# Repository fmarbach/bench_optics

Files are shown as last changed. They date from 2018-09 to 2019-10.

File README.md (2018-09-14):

## Basic Bench Optics
The repository contains the Mrsic-Flogel optics practical handout. 
This is based on the [TENSS](http://www.tenss.ro/) basic [bench optics exercises](https://github.com/tenss/bench_optics). 
You can find the latest PDF of the hand-out in the project's [Releases](https://github.com/BaselLaserMouse/bench_optics/releases).

Parts lists are supplied in `.txt` files separate from the `.tex` and `.pdf`.

### Contributing
The handout is written in Latex. 
Please do not push PDFs of the built handout to the repository because it bloats the repository.
Instead, you can upload PDFs to a release.

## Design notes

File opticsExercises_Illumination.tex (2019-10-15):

%%%%%%%%%%%%%%%%%%%%%%%%%%%%%%%%%%%%%%%%%%%%%%%%%%%%%%%%%%%%%%%%%%%%%%%
%%%%  Load the document class and packages                         %%%%
%%%%%%%%%%%%%%%%%%%%%%%%%%%%%%%%%%%%%%%%%%%%%%%%%%%%%%%%%%%%%%%%%%%%%%%
\documentclass[a4paper]{report}
\usepackage{epsfig}            % to insert PostScript figures
\graphicspath{ 
  {figures/} 
}

%Change figure names
\renewcommand{\figurename}{Fig}

\usepackage[bf,footnotesize]{caption} % make captions small and label bold

\addtocounter{chapter}{1} %Because starting at zero is silly
\makeatletter
\renewcommand{\thesection}{\@arabic\c@section}
\renewcommand{\thefigure}{\@arabic\c@figure}
\makeatother

\usepackage[a4paper,margin=2.7cm,tmargin=2.5cm,bmargin=2.5cm]{geometry} 
\usepackage{textcomp}          % To make nice degree symbols and others\usepackage[bf,footnotesize]{caption} % make captions small and label bold
\usepackage{wrapfig}
%to produce the clickable references along the left in Acroread. This
%package must be included last. 
\usepackage[ps2pdf,bookmarks=TRUE]{hyperref} 

\usepackage{wasysym}

%%%%%%%%%%%%%%%%%%%%%%%%%%%%%%%%%%%%%%%%%%%%%%%%%%%%%%%%%%%%%%%%%%%%%%%
%%%%  Hypertext references for Acrobat                             %%%%
%%%%%%%%%%%%%%%%%%%%%%%%%%%%%%%%%%%%%%%%%%%%%%%%%%%%%%%%%%%%%%%%%%%%%%%
\hypersetup{
pdfauthor = {SWC},
pdftitle = {Optics Exercises},
pdfkeywords = {optics, lenses, refraction, reflection, dispersion,
  telescope, microscope},
pdfcreator = {LaTeX with hyperref},
pdfproducer = {dvips + ps2pdf}
           }

\begin{document}

%set the number of sectioning levels 
\setcounter{secnumdepth}{2}

\begin{center}
\textbf{\Large{Optics Bench Exercises \\ \vspace{5mm} Building a brightfield microscope}}
\end{center}

\vspace{10mm}

The goal of this exercise is to build a brightfield microscope with K\"{o}hler illumination. We will do this in steps to understand the importance of illuminating the sample uniformly and from a wide range of angles. Important: think about WHY we make you place specific parts in a specific order.

\section{Critical illumination of a sample}
In critical illumination the light source is focused onto the specimen.
This provides illumination from a range of angles but has a major drawback which will become apparent soon. 

\subsection{Optical axis}
We will first create an 'optical axis' using a laser pointer - this will help us align the optics. Set the laser at one end of the rail and align the beam with the rail (horizontal and centred) using a single iris:
\begin{itemize}
    \setlength\itemsep{0.1em}
    \item Set the iris to a height suitable for adding 2'' optics. You can mount the iris to a $75~mm$ post and use a $50~mm$ post holder. 
    \item Clamp the laser pointer to one end of the rail.
    \item With the iris closest to the pointer, \textit{move/translate} the pointer until it goes through the iris. 
    \item Slide the iris to the other end of the rail and \textit{tilt} the pointer until it goes through the iris. 
    \item Repeat until the beam is parallel with the rail. 
\end{itemize} 

\begin{figure}[h]
\center

\caption{Aligning a laser beam to the rail using an iris.}
\label{fig:beam_iris}
\end{figure}

\clearpage

\subsection{Imaging optics}
Once you're done, place a positioning collar around the iris post so you can retain its height even if you have to remove it from the post holder. We start at the end of the microscope, with the tube lens and objective (Fig.~\ref{fig:beam_obj_tube}). 

\begin{itemize}
\item Hint: In addition to the iris, use `back reflections' of the laser to align optics
\item Slide the iris to the end of the rail. 
\item Place the $f=300~mm$ lens $1f$ from the iris and adjust it until the beam goes through the iris. This is your `tube lens'.
\item Place the 4x objective before the tube lens and align it such that the beam (now expanded) again goes through the iris. What is the magnification of your imaging system?
\item Why are we starting from the back of the microscope? Why the tube lens first?
\end{itemize}

\begin{figure}[h]
\center

\caption{Aligning the tube lens and objective with the beam.}
\label{fig:beam_obj_tube}
\end{figure}

\subsection{Basic illumination optics}
Let's place a sample and illuminate it with an LED, completing our simple microscope.

\begin{itemize}
\item Hint: Use $30~mm$ or $40~mm$ posts for the 2'' lenses, sample holder, and card holder.
\item Place your sample holder in front of the objective (about mid-rail)
\item Place the LED and choose one of the 1''{\diameter} $f=25~mm$ or $f=35~mm$ lenses to direct light onto the sample. Can you see the image of the LED? Where does the image form?
\item At the other end of the rail where the iris was, place a viewing screen onto which you will form an image - move the objective to focus.
\end{itemize}

The above arrangement is a simple microscope. How can you modify the illumination to make it brighter? Discuss with a TA and Implement it.
\\

You now have an infinite conjugate illumination system, giving you control over the illumination NA by placing an iris in the infinite space. Draw the ray diagram to predict what effect this has on the image. Test it with a sample! (Fig.~\ref{fig:critical_iris}).
\\

\subsection{Upgrade to K\"{o}hler illumination}
Discuss what is missing/wrong with your microscope. 

\begin{itemize}
	\item Use your K\"{o}hler notes to reason through this and implement the necessary changes
	\item Find ways to verify that your microscope is well aligned (optics placed in correct positions). Do you have independent control over illumination field and NA?
	\item Add the camera, check out different samples
	\item Impress a TA with your accomplishment
	\item Switch to a 10x objective - what determines how well you can image the sample? What is better compared to the 4x?
\end{itemize}

\begin{figure}[h]
\center


\caption{Critical illumination with two lenses. 
There is an iris after that collector lens that is open on the left image and closed on the right image. 
Note how closing the iris restricts the range of angles reaching the sample.}
\label{fig:critical_iris}
\end{figure}

\vspace{30mm}
You have finished! Unfortunately, the princess is another castle. See you tomorrow.

\clearpage

\section{Reference: K\"{o}hler Illumination}
K\"{o}hler illumination is an important and commonly used technique in light microscopy, as it provides even illumination of the sample whilst ensuring the light source (e.g. the bulb filament) is not visible. 
This is achieved by adding a third lens, the field lens, before the condenser so that the image of the light source is out of focus at the sample. 
Since the source is out of focus, the illumination is uniform. 
Instead, the image is formed at $1f$ from the field lens. 
The condenser is then located at $1f$ from this image (as in a beam expander) so collimated (i.e. out of focus) light reaches the sample. 

The key to understanding K\"{o}hler illumination is to consider the two sets of conjugate planes in the system (Fig.~\ref{fig:koehler}). 
The \textbf{sample} is, of course, conjugate with the image plane but it also conjugate with a point $1f$ from the collector lens ($f_{CL}$ in Fig.~\ref{fig:koehler}). 
The \textbf{light source} is conjugate with a location between the field lens and the condenser ($f_F$ and $f_{CO}$ in Fig.~\ref{fig:koehler}). 
The light source is also conjugate with the objective back aperture (not shown in Fig.~\ref{fig:koehler}). 

\begin{figure}[ht]
\center

\caption{K\"{o}hler Illumination. 
The blue lines indicate the conjugate relationship between the sample plane and the location of the field diaphragm.
The yellow lines indicate the conjugate relationship between the light source plane and the location of the aperture diaphragm.
}
\label{fig:koehler}
\end{figure}

At the two conjugate planes in the illumination path are two irises (diaphragms). 
The \textbf{field diaphragm} is at $1f$ before the field lens, in the point conjugate with the sample. 
The field lens and condenser lens form an infinite conjugate system that image the field diaphragm onto the sample. 
The field diaphragm appears in focus at the sample and is used to regulate the area of illumination. 
This helps to improve contrast by minimizing stray light. 
Remember, the The \textbf{f}ield planes are the image \textbf{f}orming planes. 

The \textbf{aperture diaphragm} is located in the plane conjugate with the light source. 
i.e. it is located where an image of the light source is formed. 
Opening and closing this diaphragm regulates which regions of the light source can contribute to the illumination. 
Closing the diaphragm blocks off-axis regions of the light source and stops them from generating the more oblique rays that come out of the condenser. 
Closing the aperture diaphragm reduces the NA of the illumination and increases depth of field. 

\clearpage

The completed arrangement of the components is shown in Fig.~\ref{fig:koehler_completed}. 
The components will be arranged in the following order and are all at $1f$ from each other (Fig.~\ref{fig:koehler}):
\begin{enumerate}
\setlength\itemsep{0.1em}
\item Collector lens
\item Field diaphragm.
\item Field lens ($f=60$)
\item Aperture diaphragm
\item Condenser lens ($f=60$)
\item The objective and tube lenses as before.
\end{enumerate}

\begin{figure}[h]
\center

\caption{The completed K\"{o}hler illumination assembly on a rail.}
\label{fig:koehler_completed}
\end{figure}

\end{document}

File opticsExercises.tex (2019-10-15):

%%%%%%%%%%%%%%%%%%%%%%%%%%%%%%%%%%%%%%%%%%%%%%%%%%%%%%%%%%%%%%%%%%%%%%%
%%%%  Load the document class and packages                         %%%%
%%%%%%%%%%%%%%%%%%%%%%%%%%%%%%%%%%%%%%%%%%%%%%%%%%%%%%%%%%%%%%%%%%%%%%%
\documentclass[a4paper]{report}
\usepackage{epsfig}            % to insert PostScript figures
\graphicspath{ 
	{./figures/} 
}

%Change figure names
\renewcommand{\figurename}{Fig}

\usepackage[bf,footnotesize]{caption} % make captions small and label bold

\addtocounter{chapter}{1} %Because starting at zero is silly
\makeatletter
\renewcommand{\thesection}{\@arabic\c@section}
\renewcommand{\thefigure}{\@arabic\c@figure}
\makeatother

\usepackage[a4paper,margin=2.7cm,tmargin=2.5cm,bmargin=2.5cm]{geometry} 
\usepackage{textcomp}          % To make nice degree symbols and others\usepackage[bf,footnotesize]{caption} % make captions small and label bold
\usepackage{wrapfig}
%to produce the clickable references along the left in Acroread. This
%package must be included last. 
\usepackage[ps2pdf,bookmarks=TRUE]{hyperref} 

%%%%%%%%%%%%%%%%%%%%%%%%%%%%%%%%%%%%%%%%%%%%%%%%%%%%%%%%%%%%%%%%%%%%%%%
%%%%  Hypertext references for Acrobat                             %%%%
%%%%%%%%%%%%%%%%%%%%%%%%%%%%%%%%%%%%%%%%%%%%%%%%%%%%%%%%%%%%%%%%%%%%%%%
\hypersetup{
	pdfauthor = {SWC},
	pdftitle = {Optics Exercises},
	pdfkeywords = {optics, lenses, refraction, reflection, dispersion,
		telescope, microscope},
	pdfcreator = {LaTeX with hyperref},
	pdfproducer = {dvips + ps2pdf}
}

\begin{document}

	%set the number of sectioning levels 
	\setcounter{secnumdepth}{2}
	
	\begin{center}
		\textbf{\Large{Optics Bench Exercises: Image Formation}}
	\end{center}
	
	\section{Introduction}
	The goal of these exercises is to nurture an understanding of image formation, conjugate planes, and how multiple lenses interact in simple optical setups.

	\section{Before beginning}
	\begin{itemize}
		\item \textbf{Do not} force parts together. All parts should screw together or fit together easily.
		\item \textbf{Do not} over-tighten screws. Gentle pressure with a long-handled Allen key is sufficient. 
		\item \textbf{Do not} touch the coated surface of mirrors or optical filters. 
		\item Each group is responsible for tidying and organising their optical set at the end of the week. All parts should be present and in their correct locations as shown on the course wiki page. 
		
	\end{itemize}
	
	\section{Equipment usage notes}
	The black post holders mount to the rail carriages via a short cap screw as shown in Fig.~\ref{fig:post}. 
	The carriages can then be attached to the rail, on which they can slide up and down. 
	Use the lens tool to secure lenses in lens holders. 
	`SM2' refers to two inch optics and associated accessories. 
	`SM1' refers to one inch optics and associated accessories. 
	
	\begin{figure}[h]
		\center
		
		
		
		\caption{A post holder bolted to a rail carriage (left \& middle).
			The lens tools secure lenses in the holders using the rings (right).}
		\label{fig:post}
	\end{figure}

	\clearpage
	
	\section{Image Formation}
	An image is formed when all light rays leaving one point (or region) of the object arrive at some other defined point (or region) \textit{regardless of the angle of the ray}. 
	This is illustrated in Fig.~\ref{fig:imageforming}, where the brain cell on the left is imaged through an idealised thin lens (blue) to form the minified inverted image on the right. 
	All light rays leaving the brain cell's dendrite converge onto the inverted dendrite. 
	Each point in the image plane is illuminated by rays coming from a corresponding point in the object. 

	\begin{figure}[h]
		\center
		
		\caption{Simple image formation using one idealised thin lens (blue). 
			The focal length of the thin lens is $f$, object distance is $s_o$ and image distance is $s_i$. 
			The upper ray (parallel to the optical axis on the left) passes through the focal point (denoted as a dot) on the right side of the lens, the middle ray (passing through the centre of the lens) is unrefracted, and the lower ray passes through the focal point on the left side of the lens, and comes out parallel to the optical axis on the other side. 
		}
		\label{fig:imageforming}
	\end{figure}
	
	As the distance between the object and lens ($s_o$) is varied, the distance between the lens and image ($s_i$) also changes. This relationship is determined by the lens focal length ($f$) using the thin lens equation.
	
	\begin{equation}
	\frac{1}{s_o} + \frac{1}{s_i} = \frac{1}{f}
	\label{eq:thinlens}
	\end{equation}
	
	Sign conventions follow cartesion coordinates: $f>0$ for convex lenses, $f<0$ for concave lenses, $s_o$ is always $>0$, $s_i>0$ for real images, and $s_i<0$ for virtual images.
	Transverse distances above the optical axis are $>0$. Distances below are negative. 
	
	\vspace{2.5em}
	You will need to get comfortable with drawing ray diagrams, since you will do this later to explain what you observe on the bench.
	Copy the diagram in Fig.~\ref{fig:imageforming}.
	Draw the three cardinal rays:
	\begin{itemize}
		\item The ray parallel to the optical axis goes through $f$ on the image side.
		\item The ray that passes through the centre of the lens travels undeflected.
		\item Finally, the ray that goes through $f$ on the object side leaves the lens parallel to the optical axis on the image side. 
	\end{itemize}

	\clearpage

	\subsubsection{1. Determine the focal length of a convex lens }
	For the next few exercises you will use an LED as both a light source and an object to image.
	You will form various images of the LED emitter. 
	Your first task is to set up the LED on the optical rail:
	
	\begin{itemize}
		\item Attach a post holder to a rail carriage (Fig.~\ref{fig:post}) and place this on the rail. 
		\item Attach a 50~mm post to the white LED glued to a cage plate and place this in the post holder. 
		\item Power the LED using the ThorLabs LED driver. You will need the LED power cable.
	\end{itemize}

	Now choose a lens with a focal length of about $f=100~mm$ and attach the lens to a lens holder using the lens wrench and a retaining ring (this should already be in the lens holder).
	Mount the lens on another carriage and attach to the rail next to the LED. 
	Get the LED aligned with the middle of the lens (precise alignment isn't important). 
	
	You will use this lens to form an image of the LED.
	This is called \textbf{finite conjugate} imaging because the image is paired (i.e. conjugated) with an object at a finite distance from it.
	The image and sample planes are said to be \textbf{conjugate planes}.
	You will be able to form an image on a piece of card or paper if the distance between the lens and LED ($s_o$) is $>1f$.
	The image will be of the LED emitter, which  usually looks like a small bright square, often with fine lines going across it. 
	If all you see is a blur, you have not formed an image.
	
	\begin{itemize}
		\item Place the lens $<1f$ from the LED and use a piece of card on the other side of the lens to verify that no image is formed at any distance from the lens.
		\item Why is no image formed? 
		Hint: draw a diagram with the object at $<1f$. Plot just two rays: the undeflected ray and the ray coming out parallel with the optical axis and then going through $1f$ on the image side. 
		How do the rays behave after they have passed through the lens?
		
		\item Verify that an image is formed when the lens is $>1f$ from the LED: place a card very far from the LED (e.g. at $10f$ or $20f$) and slowly move the lens away from the LED. 
		What is the distance between the LED and the lens at which you see an image? 
		It should be just over $1f$.
		
		\item You could use the above approach to estimate the focal length of an unknown lens, however it's hard to tell when the source is at $1f$. 
		What is an easier way of estimating focal length? (Hint: you may not need the rail)
		
		\item What is the value of $s_i$ when $s_o=2f$?
	\end{itemize}

	\clearpage
	
	\subsubsection{2. Magnifying the image}
	As you might recall, the size of the image of the LED emitter varied with $s_o$.
	A lens produces images of different magnifications depending on $s_o$; an image can always be formed when $s_o>f$. 
	The magnification of a lens is calculated as follows:
	
	\begin{equation}
	M = \frac{h_i}{h_o} = \frac{s_i}{s_o} = \frac{f}{s_o-f}
	\label{eq:mag}
	\end{equation}
	
	A value of $M=1$ would mean unitary magnification (the image is the same size as the object). 
	Negative numbers indicate an inverted image.
	
	To begin thinking about magnification, hand-draw the ray diagram (as in Fig.~\ref{fig:imageforming}) for the smallest and largest values of $s_o$ that you used above. 
	Make sure to give yourself plenty of room. 
	Hint: You will run out of paper if you use values too close $1f$.
	If you're stuck, choose $1.5f$ and $4f$.
	Note the changing angles of the rays and how they lead to different image sizes as $s_o$ changes. 
	We will now see what happens when the rays come from infinity:
	
	\begin{itemize}
		\item Mount a lens of about $f=60~mm$ in a holder and attach a post to it. 
		Use it to form an image of the room lights on a piece of paper.
		The image is formed at $1f$.
		\item Repeat with a lens of about $f=100~mm$ lens. 
		What two things do you notice about the image? 
		\item Fig.~\ref{fig:outside} models the situation you saw. Satisfy yourself that this provides a reasonable explanation. 
		\item Go back to the lens and LED.
		Calculate the values of $s_o$ and $s_i$ which produce $M=-4$ (remember, negative just means inverted) for a $f=100~mm$ lens. 
		Measure the size of the LED image and so calculate the size of the LED emitter. 
		\item Remember the value of $s_i$ when $s_o=2f$? Therefore what is $M$ when $s_o=2f$?
	\end{itemize}

	\begin{figure}[h]
		\center
		
		\caption{Images formed at $1f$ from light originating at infinity. 
			The top is a $f=150~mm$ lens and the bottom a $f=50~mm$ lens.
			Light from different regions of the object arrive in parallel rays that come in at different angles (green and blue). 
			Each set of parallel rays come into focus at a point, satisfying the image-forming condition. }
		\label{fig:outside}
	\end{figure}

	What you have covered above demonstrates an important property of lenses: that they work the same both forwards and backwards.
	Recall the definition of an image-forming condition: \textbf{light rays leaving one point (or region) of the object arrive at some other defined point (or region)}.
	This is why no image was formed when the LED was at $s_o=f$, since rays leaving the lens are parallel and do not converge on the other side. 
	However, you \textit{were} able to form an image at $s_i=f$ when the object was very far away. 
	The ray diagrams of these two conditions are \textit{identical}--the only difference is that the object is at $1f$ in the first case and at infinity in the second case.
	
	\clearpage

	\subsubsection{3. Virtual images}
	At distances $s_o<f$, you were unable to form an image of the sample on the card because the rays emerging from the other side \textit{diverged}.
	\begin{itemize}
		\item Place the LED at $0.5f$ from a lens of your choice, observe the light diverging as it exits the lens.
		\item Draw the ray diagram for this $0.5f$ scenario:
		Draw the ray that leaves the tip of the object and continues undeflected through the middle of the lens. 
		Draw the ray that travels parallel to the optical axis and goes through $1f$ on the other side.
		See how these rays diverge. 
	\end{itemize}
	
	It would seem that no image is formed yet, surprisingly, a \textit{virtual image} is formed on the same side of the lens as the object. 
	This may sound like a peculiar concept, but you are already familiar with virtual images as this is how you see images in flat mirrors (Fig.~\ref{fig:mirror}). 
	The extended rays in the case of the mirror can be created from the \textit{diverging} rays from the object. 
	In the case of the the lens at $s_o<f$ we also have diverging rays and so can also draw extended rays as we did for the mirror. 
	Add the extended rays to your ray diagram by continuing the rays on the object side of the lens until they converge. 
	A virtual image is formed where they converge.
	What does your diagram tell you about the magnification of the virtual image?
	Verify this: pick up the lens, place it $<1f$ from an object and look through it.
	\begin{figure}[h]
		\center
		
		\caption{A virtual image of the bottle is created on the far side of the mirror. 
			This is described by the dotted lines which are `extended rays' that are used to form the virtual image. }
		\label{fig:mirror}
	\end{figure}
	
	A virtual image is also formed by a negative (concanve) lens, as shown in Fig.~\ref{fig:neglens}. 
	Examine the ray diagram of the negative lens. 
	What do you predict you will see if you look through a negative lens?
	Verify this with the $f=-50~mm$ lens.
	\begin{figure}[h]
		\center
		
		\caption{Ray diagram of a negative lens.}
		\label{fig:neglens}
	\end{figure}
	
	In summary, a \textbf{real image} is formed on the opposite side of the lens to the sample. 
	This allows the detector to be physically separated from the sample, which is rather useful.
	A \textbf{virtual image} is formed on the \textit{same} side of the lens as the object. 
	
	\clearpage
	
	\subsection{Infinite Conjugate}
	The \textbf{infinite conjugate} refers to the situation where the object is located at a distance of $1f$ from a lens (Fig.~\ref{infiniteConjugate}). 
	In this scenario the rays leaving the lens are parallel and do not converge, so this is not an image forming condition. 
	Instead, the image can be considered to be infinitely far away (hence the name). 
	If a second lens is added, then an image can be formed. 
	The magnification of the image is defined as Eq.~\ref{eq:magIC}. 
	This arrangement is useful because the image is always formed at $1f$ from the second lens irrespective of the distance between the lenses.
	Most microscope objectives are designed to work in this configuration since it allows filters to be added into the infinite space without altering the location of the image plane. 
	Such objectives are known as `infinity corrected', since they are designed to produce their best images with the sample at $1f$.
	
	\begin{equation}
	M=-\frac{f_2}{f_1}
	\label{eq:magIC}
	\end{equation}
	
	\begin{figure}[h]
		\center
		
		\caption{Two views of an infinite conjugate system made up of two $f=100~mm$ lenses. 
			The upper image shows on-axis rays only. 
			Note the rays are parallel in the infinite space.
			The lower diagram shows two additional sets of rays which arise from different off-axis locations and converge into corresponding locations in the image plane. }
		\label{infiniteConjugate}
	\end{figure}
	
	\begin{itemize}
		\item Set up two lenses with different focal lengths on the rail to build the infinite conjugate. 
		Ensure that the first lens is at $1f$ from the LED before placing the second lens. 
		\item Place a screen at the $f$ of the second and hold it in place with the post-mounted clip.
		\item Verify the consequences of the infinite space by moving the second lens and maintaining the screen at $f$ of the second lens. 
		What happens to the image size?
		\item Swap the first lens with one of a different focal length. 
		Verify that the image size changes in the manner in which you expect. 
	\end{itemize}

	\clearpage

	\subsection{Beam expanders}
	Lenses can be used to expand the diameter of a light beam, such a laser.
	Expanders can be built using either two convex lenses (Fig.~\ref{beamExpander1}) or a convex and concave lens (Fig.~\ref{beamExpander2}). 
	In both cases the lenses are set up such that their focal points coincide (i.e. they are separated by the sum of their focal lengths). 
	The image formed by the first lens is imaged at infinity by the second lens.
	The degree to which a beam is expanded is given by:
	\begin{equation}
	\frac{d_2}{d_1}=\frac{f_2}{f_1}
	\label{eq:beamExp}
	\end{equation}
	
	\begin{figure}[h]
		\center
		
		\caption{Beam expander with two convex lenses.}
		\label{beamExpander1}
	\end{figure}
	
	\begin{figure}[h]
		\center
		
		\caption{Beam expander with one convex and one concave lens.}
		\label{beamExpander2}
	\end{figure}
	
	We need collimated light (parallel rays) entering the system, so swap the LED for a laser pointer.
	You will align your laser to the rail (i.e. have the beam traveling parallel with the rail). 
	The lenses will then be aligned with respect to the beam. 
	This is an easy way of producing a well-aligned optical system and you will use the technique again and again throughout the course.
	The procedure is as follows:
	
	\begin{itemize}
		\item The laser is mounted in a 1'' tip/tilt mount. Screw this into a 1'' cage plate and attach this to one end of the rail via a 75 mm post (Fig.~\ref{fig:mounted_laser}).
		\item Power on the laser using the attached USB cable.
		\item Place the iris in a post next to the laser pointer, close it and adjust the height of the laser pointer and iris so the beam goes through the hole. 
		\item Slide the iris to the other end of the rail. 
		\item \textit{Rotate} the post the laser pointer sits on so it points at the iris aperture. Use the tip/tilt adjuster screws for fine adjustment.
		\textbf{Do not translate the laser pointer up and down.}
		\item Slide the pointer back down the rail and confirm that the beam still passes through hole. 
		If not, \textit{translate} the laser pointer's post up and down, then repeat the previous step.
	\end{itemize}
	
	\begin{figure}[h]
		\center
		%%\includegraphics[width=3in]{mounted_laser.eps}
		\caption{Laser mounted on a post.}
		\label{fig:mounted_laser}
	\end{figure}

	Now you will build a 3x beam expander $f=300~mm$ lens and an $f=100~mm$ lens. 
	These will be placed at the sum of their focal lengths and the laser pointer will be used as a guide for placing the lenses. 
	
	\begin{itemize}
		\item Place two more rail carriages onto the rail, between the iris and the laser pointer. 
		\item Place the $f=100~mm$ lens onto the post carriage nearest the laser and position the iris roughly $1f$ from the lens.
		\item You will know the lens is at the correct height because the beam will hit the middle of the iris. 
		If you look carefully at the lens surface, you can also judge the height by looking at the back-reflection of the beam on lens surface. 
		\item Slide the iris down the rail and complete the expander with the $f=300~mm$ lens. Again, use the iris as a target to judge lens height.
		\item Make sure that the two focal points coincide by checking that the exit beam remains collimated (does not diverge or converge)
		at all distances from the second lens. 
		\item Measure the size of the expanded beam and so calculate size of the unexpanded beam.
		\item Swap out the $f=100~mm$ lens with the $f=-50~mm$ concave lens. Verify that the expanded beam diameter doubles. 
		What advantages does the negative lens add?
		\item Build a beam expander to yield the maximum magnification your optics kit allows (e.g. $f=300~mm$ and $f=30~mm$ to yield 10x). 
		The beam expander you have built also goes by another common name.  What is it? 
		Hint: think about what happens to beams that do not travel on-axis (Fig.~\ref{fig:telescope}).
		Once you've figured it out, remove the laser pointer and use your device. 
	\end{itemize}

	\begin{figure}[h]
		\center
		
		%\includegraphics[width=3in]{Telescope_Obj.eps}
		%\includegraphics[width=3in]{TelescopeEyepiece.eps}
		\caption{A beam expander composed of an $f=300~mm$ lens and an $f=25~mm$ lens. 
			In addition to the collimated beam arriving on-axis (blue), two off-axis beams are shown in different colors.
			Note how the angles of the beams leaving the $f=25~mm$ are substantially larger.}
		\label{fig:telescope}
	\end{figure}
	
	\clearpage

	\subsection{Optics Challenge}
	Arrange 4 lenses, one of which must be a negative lens, so as to form a de-magnified, real, upright image. Hints: 
	\begin{itemize}
		\item Space will be a problem: the lenses will take up the whole rail and so you will need to place the target and screen outside of the rail.
		\item Use a bright light source to illuminate your target or the image will likely be dim. 
		\item There are multiple solutions to this problem.
	\end{itemize}

	\subsection{Bonus Exercise: Compound Lenses \& Optical Aberrations}
	\begin{wrapfigure}{R}{0.22\textwidth}
		\begin{center}
			
			
		\end{center}
		\vspace{-100pt} 
	\end{wrapfigure}
	In this optional exercise you'll explore image aberrations and see why camera lenses, microscope objectives, and eyepieces contain multiple lenses spaced closely together. 
	You will do this by building a variety of simple telescopes and assessing their image quality.
	After this exercise you will have learned:
	\begin{itemize}
		\setlength\itemsep{0.15em}
		\item Why thin lens ray tracing does not capture aberrations.
		\item What is chromatic aberration and how it can be corrected.
		\item What are spherical aberration (SA) and coma.
		\item How aberrations can be reduced by using smaller ray angles.
	\end{itemize}

	\subsubsection{Limitations of the thin lens approximation}
	The ray tracing you've learned is good for planning simple optical systems but offers no information about image quality. 
	This is because your ideal `thin lenses' always observe the image forming condition: all rays leaving a point on the sample plane converge onto a point on the image plane. 
	In reality the image forming condition does not always hold. 
	Rays hitting the lens at steeper angles will come into focus at a position other than that predicted by thin lens ray tracing. 
	This is worse for steeper ray angles and more curved lenses. 
	Image `\textbf{aberrations}' occur when rays leaving a point in the sample do not all converge in the image plane.
	Rays instead converge in different locations according to a systematic pattern which depends upon the form of the aberration. 
	The the three most common aberrations are chromatic aberration, spherical aberration, and coma (Fig.~\ref{fig:aberrations}). 
	
	\begin{figure}[h]
		\center
		
		\caption{ 
			Chromatic aberration sees light of different wavelengths coming into focus at different distances from the lens.
			Spherical aberration sees on-axis light (that parallel to the optical axis) having different focal lengths depending upon distance from the optical axis. 
			Coma is the situation where off-axis light does not come into focus in the same spot. Coma does not occur for rays traveling along the optical axis.}
		\label{fig:aberrations}
	\end{figure}

	\subsubsection{Chromatic aberration}
	Blue light is refracted more strongly than red light and so the focal length of a lens is wavelength dependent. 
	Lenses therefore have shorter focal lengths for blue light than red light (Fig.~\ref{fig:aberrations}).
	This leads to a pronounced wavelength-dependent blurring of the image known as chromatic aberration. 
	You will now build a telescope on the 500 mm optical rail:
	\begin{itemize}
		\item Use an f=300~mm for the objective and an f=25~mm for the eyepiece. 
		\item Look through your telescope at an object across the room. How does the chromatic aberration manifest itself?
		\item Ask for the f=300~mm achromat and swap your singlet lens with this. Observe the image again.
	\end{itemize}
	
	\textbf{How does it work?} 
	The first element of the achromat is a positive lens that will converge light. 
	The second element is a negative lens that will diverge light.
	This second element has a lower power and so together the elements of the achromat constitute a positive lens. 
	The two elements are made of glass with different indexes of refraction. 
	The second (negative) element has a stronger index of refraction. 
	Thus, the second lens diverges blue light more strongly than the first lens can focus it.
	This balancing act is finely tuned to bring red and blue light into focus at the same spot.
	
	Coarsely speaking, the second lens of the achromatic doublet disperses light in the \textit{opposite direction} to the first lens in order to bring different wavelengths into a common focus. 
	\textbf{Aberrations are generally corrected by adding an element which introduces the opposite aberration.}

	\subsubsection{Spherical Aberration \& Coma and Ray Angles}
	Look through your telescope and pay attention to how the image quality varies across the field of view. 
	What do you see?
	What you see is likely due to various different aberrations. 
	Let's try to clean up the image. 
	
	Examine Fig.~\ref{fig:aberrations}, whilst it doesn't show how SA and coma arise it does allow us to predict that these aberrations will be less prominent if the outer rays are removed. 
	Place an iris on a rail carriage and locate it around 15 cm behind the objective lens. 
	Close the iris whilst looking through the telescope. 
	As the iris closes, fine features at the edges of the field will become sharper but the field of view doesn't change. 

	\subsubsection{Compound Eyepieces}
	Using an iris (known as a `pupil') to reduce ray angles is a common approach for taming aberrations but it is limited since it of course also reduces light. 
	A better approach is to choose lenses such that you avoid introducing aberrations in the first place. 
	You will now replace the $f=25~mm$ lens with a compound lens of similar focal length (Eq.~\ref{eq:compoundLensF} shows how to calculate the effective focal length of two thin lenses separated in air by some distance $d$). 
	A compound lens is one where the optical elements are spaced closely together. 
	Ask for one of the two compound lenses: one is is composed of two plano-convex singlet lenses (Fig.~\ref{fig:composite}, right)
	and the other is known as a Pl\"{o}ssl eyepiece, which is composed of two closely spaced achromats. 
	In what ways has the image improved compared to the single $f=25~mm$ lens?
	Is the Pl\"{o}ssl better than the singlet pair?
	
	\begin{equation}
	\frac{1}{f} = \frac{1}{f_1} + \frac{1}{f_2} - \frac{d}{f_1f_2}
	\label{eq:compoundLensF}
	\end{equation}

	\begin{figure}[h]
		\center
		
		%\includegraphics[width=2.15in]{Plossl.eps}
		\caption{Ray diagrams of two of the eyepieces you have access to. Left: $f=25~mm$ plano-convex singlet (you might have a bi-convex version). 
			Right: $f=25~mm$ compound lens composed of two $f=50~mm$ singlet lenses. 
			Blue rays are on-axis. 
			Green rays arise from an object 1 degree off-axis. }
		\label{fig:composite}
	\end{figure}

	\textbf{Why does the compound lens clean up the image edges?} 
	The simple answer is that the singlet lens must bend off-axis light by a large amount as it exits (Fig.~\ref{fig:composite}) and this is sufficient to induce large aberrations. 
	Even in this low resolution ray diagram, you can see that the green ray is not collimated upon exiting the lens.
	The doublet lens spreads the `work' across more surfaces and so avoids introducing aberrations. 
	The green rays leaving the final surface remain collimated. 

\end{document}

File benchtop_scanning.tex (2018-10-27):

%%%%%%%%%%%%%%%%%%%%%%%%%%%%%%%%%%%%%%%%%%%%%%%%%%%%%%%%%%%%%%%%%%%%%%%
%%%%  Load the document class and packages                         %%%%
%%%%%%%%%%%%%%%%%%%%%%%%%%%%%%%%%%%%%%%%%%%%%%%%%%%%%%%%%%%%%%%%%%%%%%%
\documentclass[a4paper]{report}
\usepackage{epsfig} %to insert PostScript figures
\graphicspath{ 
  {scanningFigs/} 
}

%Change figure names
\renewcommand{\figurename}{Fig}

\usepackage[bf,footnotesize]{caption} % make captions small and label bold
\usepackage{graphicx}

\addtocounter{chapter}{1} %Because starting at zero is silly
\makeatletter
\renewcommand{\thesection}{\@arabic\c@section}
\renewcommand{\thefigure}{\@arabic\c@figure}
\makeatother

\usepackage[a4paper,margin=2.7cm,tmargin=2.5cm,bmargin=2.5cm]{geometry} 
\usepackage{textcomp}  %To make nice degree symbols and others\usepackage[bf,footnotesize]{caption} % make captions small and label bold
\usepackage{wrapfig}

\begin{document}

%set the number of sectioning levels 
\setcounter{secnumdepth}{2}

\begin{center}
\textbf{\Large{Scanning Software \& Data Acquisition}}
\end{center}

\section{Introduction}

In widefield microscopy the entire field of view is illuminated and a great deal of scattered light from outside of the focal plane ends up in the image plane. 
These scattered photons create blur and reduce contrast since they fail to satisfy the image-forming condition, arriving at the image plane at a location \textit{not conjugate} with their origin.
Fluorescence-based scanning microscopy can greatly mitigate the problem of scattering. 
A laser beam is scanned across the sample where it excites fluorophore molecules. 
Emitted fluorescence is collected via the objective and detected at a photomultiplier tube (PMT). 
No image is formed on the PMT (it's a `single pixel'), instead the image is constructed \textit{post-hoc} on a computer with the spatial origin of the emitted fluorescence determined by the position of the laser beam over time.
In confocal microscopy, emitted fluorescence arising away from the focal point is rejected by a pinhole conjugate with the sample and near the PMT. 
With 2-photon microscopy, the excitation spot is highly restricted so the origin of all collected photons is known (Fig.~\ref{1pvs2p}). 

\begin{figure}[h]
\centering
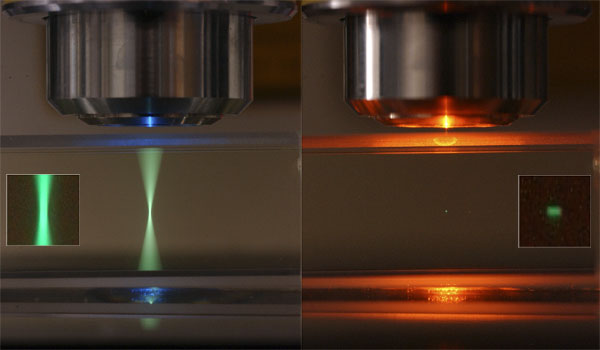
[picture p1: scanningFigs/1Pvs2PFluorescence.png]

\caption{A blue (488nm) laser of the sort used in confocal imaging excites an entire column of sample leading to green fluorescence (left).
A pulsed IR laser excites only at the focal point, as this is the only location where the density of photons is great enough for the 2-photon effect to take place.}
\label{1pvs2p}
\end{figure}

\subsection{Goals}
In the following exercises you will learn how to write simple scanning software using MATLAB and NI DAQmx in order to run a transmitted light laser scanning microscope. 
The goals of today are:
\begin{itemize}
\setlength\itemsep{0.15em}
\item Learn how to drive the scan mirrors using analog output waveforms from a data acquisition card. 
\item Learn how to syncronise analog input and output and understand how an image is produced from a photodiode signal. 
\item Become familiar with the basics of controlling National Instruments data acquisition hardware.
\item Understand how a beam expander is used to conjugate scanning mirrors onto the objective back aperture to image microscopic samples.
\end{itemize}

\clearpage

\section{Driving the scan mirrors}
A scanning microscope has two scan mirrors (`galvos'): one for $x$ and one for $y$ motion.
Each galvo is connected to a driver card that both powers it and controls the mirror position angle (Fig.~\ref{scanners}). 

\begin{figure}[h]
\centering
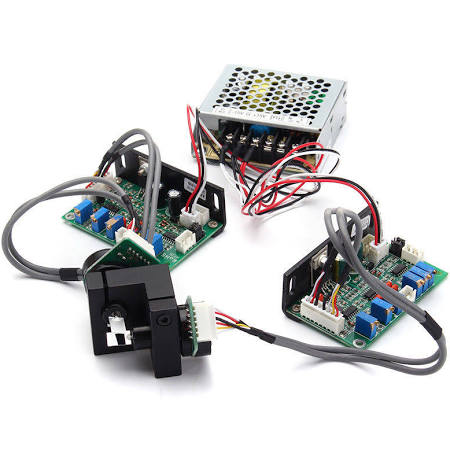
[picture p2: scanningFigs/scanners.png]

\caption{A pair of scan mirrors mounted orthogonally to each other and each connected to control card. The two control cards share a power supply.}
\label{scanners}
\end{figure}

Set up the rail as shown in Fig.~\ref{scannersOnRail}.
The scanners are bolted to the rail via the LCP11/M.
The rail carriage with the iris should be able to freely slide up and down the length of the whole rail.
The scanners need to be powered and receive a 0~V command signal. 

\begin{figure}[h]
\centering

\caption{The scanners mounted to the rail along with an iris. 
The two mirrors will route the beam into the scanner box.}
\label{scannersOnRail}
\end{figure}

\noindent
Direct the laser beam using two adjustable mirrors such that it hits the middle of the scan mirrors then comes out at 90 degrees with respect to the incoming beam (as shown in Fig.~\ref{scannersOnRail}). 
Using the iris as a target, ensure the beam runs straight down the rail. 
It's OK for our purposes if the alignment isn't \textit{perfect}: a couple of beam diameters is adequate. 
Tips:
\begin{itemize}
\setlength\itemsep{0.15em}
\item Place one routing mirror close to the scanners and the other some distance away. 
\item Have all mirrors roughly square with respect to each other before starting.
\item Use adjustment screws for fine-alignment only.
\end{itemize}

\clearpage

\subsection{Controlling the scan mirrors}

\begin{itemize}
    \item Open NI MAX (Measurement \& Automation Explorer),
        \begin{enumerate}
            \setlength\itemsep{0.15em}
            \item Select the DAQ device from the list on the left then hit `Test Panels'. 
            \item Select the `Analog Output' tab (Fig.~\ref{DAQMX}).
            \item Set `Mode' to `Voltage Sinewave Generation' and set the amplitude to about `5V'.
            \item Leave the `Rate' at `1000'. This will produce a 1~Hz sine wave.
            \item Connect the analog outputs to the osciloscope and confirm you get waveforms out of both channels. 
        \end{enumerate}

    \item Turn on the laser, copy signals to the scanner controller analog inputs and try driving the scan mirrors with the 1~Hz signal.  
    \item Set `Rate' to `50,000' to produce a 50~Hz motion. What does the outgoing beam look like now?
    \item Now try the `DC' option under `Mode' and explore what happens when you apply a variety of constant non-zero voltages (press `Update' to apply your chosen voltage to the device).
\end{itemize}

\begin{figure}[h]
\centering
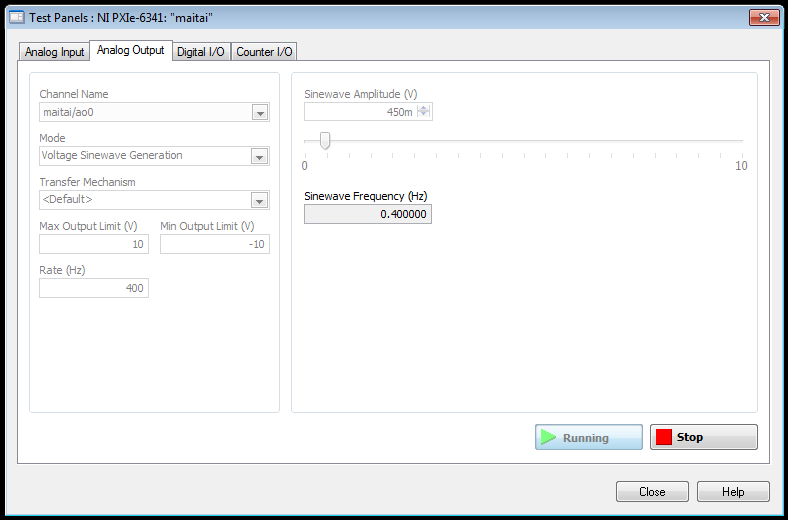
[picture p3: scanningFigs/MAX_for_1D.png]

\caption{The NI MAX test panel for analog output.}
\label{DAQMX}
\end{figure}

\clearpage

\section{Building the scan pattern}

You will now use MATLAB to generate scan waveforms and explore how to build an effective 2-D scan pattern. 
Before starting, make the following modifications to the DAQ breakout box. 

\begin{itemize}
    \setlength\itemsep{0.15em}
    \item Copy \texttt{AO0} to \texttt{AI0} with a BNC cable. This will allow us to acquire and monitor the $x$ galvo command signal.
    \item Connect \texttt{AI1} to the galvo position output lead. This will allow us to compare the actual mirror position with the command position.
\end{itemize}

\noindent
You will now use a MATLAB class called `wavformTester' to explore different scanning waveforms.
The class is part of the SimpleMScanner\footnote{\textit{https://github.com/tenss/SimpleMScanner}} repository, which contains basic scanning software written in MATLAB.

\begin{itemize}
\setlength\itemsep{0.15em}
\item In MATLAB, run \texttt{edit waveformTester.m} to bring up the code. 
\item Run \texttt{S=waveformTester;}, which will send a sinusoidal command signal to the scanner and create an object called \texttt{S} in the base workspace.
\item At any time you can stop acquisition and disconnect from the DAQ by closing the figure window.
\end{itemize}

\noindent
With the default scan settings you should see something similar to that shown in Fig.~\ref{waveformTester01}.
You will see a red sinusoid, which is the galvo position feedback signal. 
Underneath the red trace is a black trace that represents the command signal. 
The inset blue sub-plot shows the position signal as a function of the command signal. 
The frequency of the waveform is displayed in both the window title and at the command line. 

\begin{figure}[h]
\centering
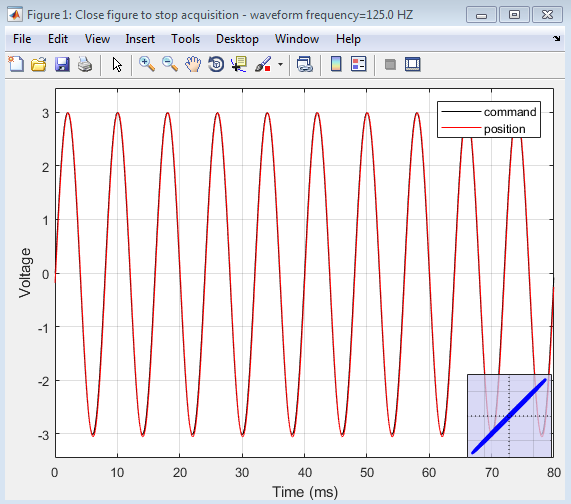
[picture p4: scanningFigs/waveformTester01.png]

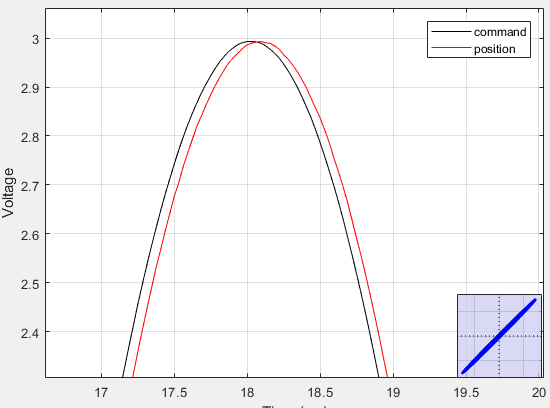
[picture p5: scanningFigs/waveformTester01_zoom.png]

\caption{Left: \texttt{waveformTester} running with default settings. 
        The waveform frequency is shown in the figure title bar. 
        The galvo command signal is shown in black and the feedback signal from the galvo control box is shown in red. 
        The inset blue plot shows the feedback signal as a function of the command signal.
         Right: A zoomed-in view showing the close correspondence between the command signal (black) and the actual galvo position (red).
         When zoomed-in you will notice the plot is regularly updating.}
\label{waveformTester01}
\end{figure}

\noindent
Read through the code and satisfy yourself that you understand how it works. 
Pay particular attention to how the waveform is built. 

\begin{itemize}
    \setlength\itemsep{0.15em}
    \item The waveform amplitude is scaled by the \texttt{galvoAmp} property.
    \item For the current sine wave, \texttt{pixelsPerLine} is the number samples in one cycle. 
    \item The waveform is repeated \texttt{numReps} times, and this many cycles are plotted at once. 
    \item The \texttt{generateScanWaveform} method builds the waveform, which may be either a sawtooth or a sine wave according to the value of \texttt{waveformType}.
\end{itemize}

\clearpage
\subsection{The effect of command signal frequency}
The scanners have inertia so their ability to follow the command waveform will depend upon its shape and frequency. 
Let's try changing the frequency. 

\begin{itemize}
\item Close the figure window (take a screenshot first if you want to compare before and after) and edit the \texttt{sampleRate} property.
Increase it from the default 32E3 to 128E3 (meaning $128~kS/s$). 
\texttt{sampleRate} is used by the \texttt{ratecfgSampClkTiming} methods of the AI and AO DAQmx tasks to set the sample rate.
This is done in the \texttt{connectToDAQandSetUpChannels} method of \texttt{waveformTester}.
\item Re-start the \texttt{waveformTester} object (close window and run command again). 
\item Notice the larger phase lag between the position and command and how this is reflected in the blue X/Y plot. 
\end{itemize}

\noindent
Now try using fewer samples per cycle, which is the other way of increasing the mirror frequency. 
Close the figure window, set \texttt{pixelsPerLine} from the default 256 to 128, and restart.
At 128 \texttt{samplesPerLine} and $128~kS/s$ sample rate the scanner runs at $1~kHz$.

\subsection{Different waveform types}
Return the sample rate to 32E3 and the number of samples per line to 512. 
Change the \texttt{waveformType} property from `sine' to `sawtooth' and restart the \texttt{waveformTester}. 
How well is the scanner following the command waveform? 
Satisfy yourself that you understand why the blue inset plot looks as it does. 
What are the advantages and disadvantages of this new waveform for building 1-D images?
Hint: think about how the beam changes speed during the sawtooth in comparison to the sinewave.
Think also how you might build the image on the PC and how well the mirrors follow the sawtooth waveform.

\clearpage

\section{Building scan waveforms}

So far you have moved only the $x$ mirror and considered 1-D images. 
Obviously you need to move both mirrors at the same time to get a 2-D scan pattern and image full frames.
Before proceeding, let's get both mirrors moving at the same time. 
First of all, re-wire your setup so that the two analog outputs are copied to channels 1 and 2 of the oscilloscope.
\texttt{AO0} should also go to the \textit{x} mirror analog input and \texttt{AO1} to the \textit{y} mirror analog input.
Run \texttt{vidrio.AO.hardwareContinuousVoltageNoRegen\_2chans} to play out two sine waves.
Satisfy yourself that your understand why the beam motion looks the way it does based upon the oscilloscope traces.

\subsection{Acquiring a 2-D image}

In this section you will modify \texttt{waveformTester.m} in order to turn it into a simple piece of scanning software. 
The major changes will be:
\begin{enumerate}
    \setlength\itemsep{0.15em}
    \item Instead of plotting the galvo feedback signal it will need to plot an image of the sample. 
    \item It will need to drive both galvos instead of just one. 
    \item The waveforms will need to be suitable for producing an image.
\end{enumerate}

Since we will be making an image with the photodiode signal, connect the photodiode to \texttt{AI0} using a BNC cable.
You will need to produce suitable $x$ and $y$ waveforms and also to plot the photodiode signal as an image. 
Use \texttt{vidrio.AO.hardwareContinuousVoltageNoRegen\_2chans} to figure out how to add the second analog output channel.
Try to generate waveforms that will produce square images at about 0.5 frames per second. 
Start off with a fixed sample rate of 32E3 and change the frame rate by altering the image size.
Hints:
\begin{itemize}
    \setlength\itemsep{0.15em}
    \item The waveforms are stored in an N-by-2 array, where each row is a different time point. You only need to modify code in the \texttt{generateScanWaveform} method.
    \item Modify \texttt{obj.hAOTask.createAOVoltageChan} to use both channels 0 and 1.
    \item The \texttt{numReps} property can be used to set the number of scan lines per frame.
\end{itemize}

\noindent

Once you have the waveforms looking reasonable judging by the oscilloscope and the scan pattern, it's time to modify the code to handle the photodiode signal. 
To begin with, let's just ensure we can display the incoming photodide signal as a line plot.

\begin{itemize}
    \setlength\itemsep{0.15em}
    \item Modify \texttt{obj.hAITask.createAIVoltageChan} to acquire only on \texttt{AI0}.
    \item In the constructor you can remove the code for making the blue inset plot and remove the line which creates \texttt{obj.hPltDataAO1}, as we won't be plotting that channel.
    \item Modify the \texttt{readAndDisplayScanData} method to update only \texttt{obj.hPltDataAO0}. Remove lines relating to the other plots. 
    \item Allow the beam to scan over the photodiode and test the code. 
    You should see something like that shown in Fig.~\ref{lineOnPD}. 
\end{itemize}

\noindent

\begin{figure}[h]
\centering
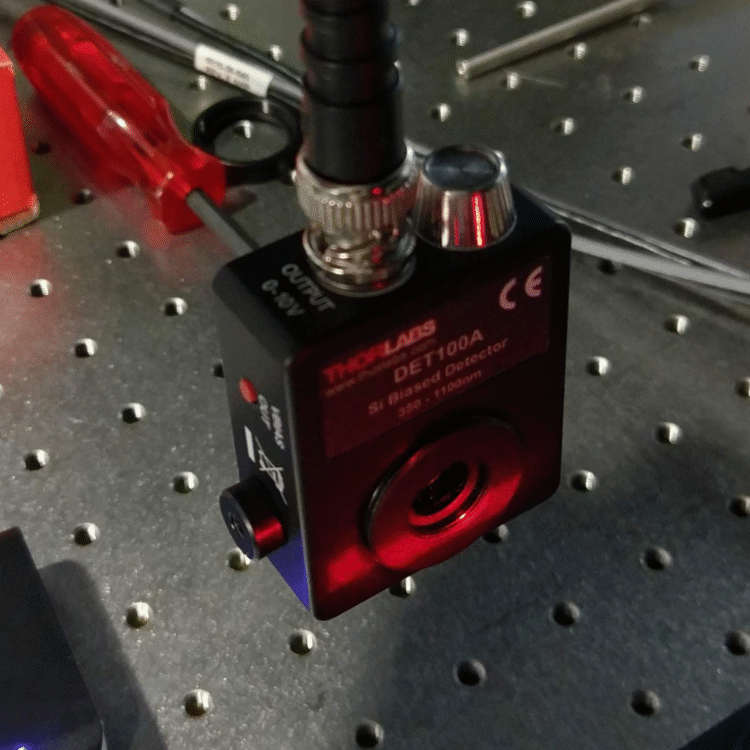
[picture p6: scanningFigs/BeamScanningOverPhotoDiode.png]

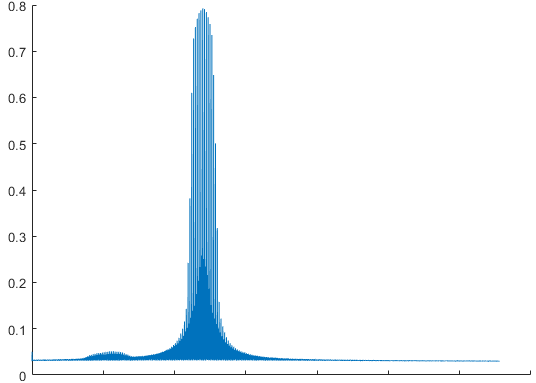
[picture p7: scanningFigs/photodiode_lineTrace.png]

\caption{Left: The beam scanning over the photodiode
         Right: The photodiode signal plotted on screen as a time trace.
         The this plot was obtained by positioning the photodiode about 30 cm from the scanners and using a waveform amplitude of about 4~V. 
         Under these circumstances the beam is only scanning over the photodiode for a short period of time, producing the peak you see in the plot. }
\label{lineOnPD}
\end{figure}

\noindent
Once you have reached the stage above, you know that you're pulling in the data correctly and all you need to do is reshape them into an image instead of a line plot.
Hints:
\begin{itemize}
    \setlength\itemsep{0.15em}
    \item In the constructor, the line \texttt{obj.hPltDataAO0 = plot(obj.hAxes, zeros(100,1), '-k');} should instead create a blank image using \texttt{imagesc}. Any size is fine.
    \item In the \texttt{readAndDisplayData} method you will need to modify the plot object's \texttt{CData} property instead of the \texttt{YData} property. 
    \item You already know what size to \texttt{reshape} the data too, since you know the number scan lines and the number of lines per frame.
    \item Minor changes, like altering the color-scale look-up table, can be made whilst the code is running.
\end{itemize}

\noindent
Place the photodiode around 30~cm from the scanners and use and amplitude of 2 or 3~V.
Fire up the code and try to get an image. 
What do you see?
Which axis in the image corresponds to the $x$ (fast) axis?
Is it what you expect? Hint: think about how the image is being assembled and how well the scanner follows the command signal.
What is odd features does the image have and how can you explain them?

\section{Obtain an image of a microscopic sample}
Place one of the small insect specimens (such as a flea) in front of the photodiode. 
Do you get an image of the flea?
Why does the image not look great?
Try using the $f=60~mm$ lens as an objective to improve the image. 
Why does the image now look better?
If you like you can also screw the $f=25~mm$ lens in front of the photodiode to collect more light. 

\begin{figure}[h]
\centering
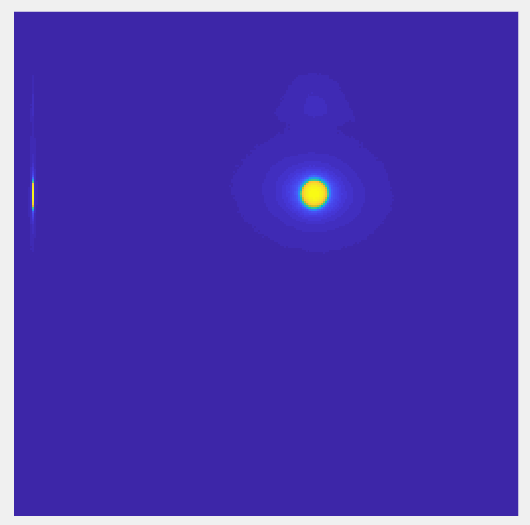
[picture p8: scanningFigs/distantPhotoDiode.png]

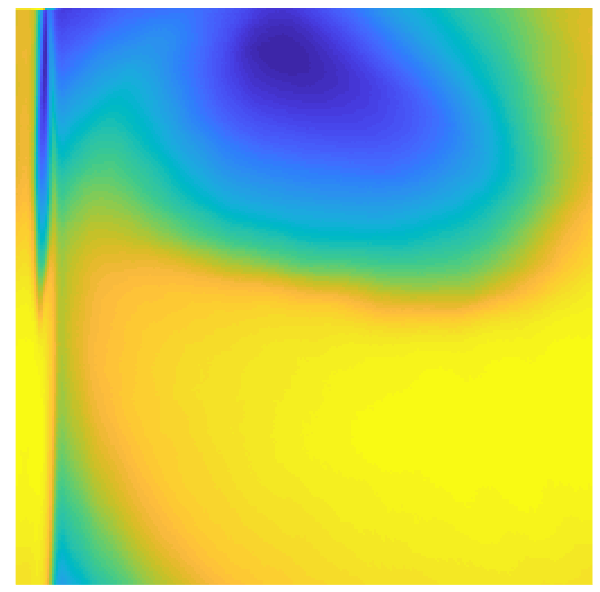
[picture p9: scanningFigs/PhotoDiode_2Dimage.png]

\caption{Left: With a large-angle scan pattern and the photodiode far from the scanners you end up with an image of the whole scan-field showing the position of the photodiode within the scan-field.
         Right: Here the scan angle is reduced to just fill the photodiode and a small piece of tape is placed on the middle of a coverslip in front of the photodiode. 
         An image of the tape piece is then be formed on the computer.}
\label{PDimage}
\end{figure}

\clearpage

\section{Imaging with increased NA}
In scanning microscopy we usually wish to fill the back aperture of the objective in order to use its full NA and get the smallest PSF. 
We use microscopy objectives, as these are very well corrected and produce a good PSF over a fairly large range of scan angles. 
How might you modify your microscope to image the sample with the 4x objective objective?
You can not just replace the $f=60~mm$ lens with the objective, as the thin laser beam would just sweep across the back of it. 
You will need to add optics between the scanners and objective in order to both expand the beam and cause it to pivot at the back aperture (Fig.~\ref{pivot}). 
Hint: recall the concept of conjugate planes from the illumination practical.

\begin{figure}[h]
\centering


\caption{Left: A scan mirror deflects a laser beam as it pivots about its axis.
         Right: In order to scan a focused spot across a sample, the beam must pivot at the back aperture of the objective. }
\label{pivot}
\end{figure}

\noindent
Place a slide containing an EM grid at the working distance of the objective. 
Place a photodiode close to the back of the slide and hook it up to \texttt{AI0} on your DAQ. 
You may get a better image with a collection lens in front of the detector, but this isn't critical\footnote{Or even K\"{o}hler, for that matter.}.
Focus the beam onto the grid as best you can by eye.
Now it's time to get an image!

\section{Optional question: correcting image artifacts}
If you have completed the above and still have time, you can consider how to get rid of scanning artifacts. 
We built images based on the command waveforms. 
In other words, we assume the beam is located where we asked it to be and we placed the pixels at that location.
Since the actual beam position does not follow the expected position, this produces artifacts. 
Try to come up with a way of correcting the image. 
Perhaps you could use the mirror feedback signal, or use the command signal but remove the non-linear portions, or some mixture of those options. 

\end{document}

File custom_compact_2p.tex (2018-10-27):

%%%%%%%%%%%%%%%%%%%%%%%%%%%%%%%%%%%%%%%%%%%%%%%%%%%%%%%%%%%%%%%%%%%%%%%
%%%%  Load the document class and packages                         %%%%
%%%%%%%%%%%%%%%%%%%%%%%%%%%%%%%%%%%%%%%%%%%%%%%%%%%%%%%%%%%%%%%%%%%%%%%
\documentclass[a4paper]{report}
\usepackage{epsfig}            % to insert PostScript figures
\graphicspath{ 
  {figs_compact2p/} 
}

%Change figure names
\renewcommand{\figurename}{Fig}

\usepackage[bf,footnotesize]{caption} % make captions small and label bold

\addtocounter{chapter}{1} %Because starting at zero is silly
\makeatletter
\renewcommand{\thesection}{\@arabic\c@section}
\renewcommand{\thefigure}{\@arabic\c@figure}
\makeatother

\usepackage[a4paper,margin=2.7cm,tmargin=2.5cm,bmargin=2.5cm]{geometry} 
\usepackage{textcomp}          % To make nice degree symbols and others\usepackage[bf,footnotesize]{caption} % make captions small and label bold
\usepackage{wrapfig}
%to produce the clickable references along the left in Acroread. This
%package must be included last. 
\usepackage[ps2pdf,bookmarks=TRUE]{hyperref} 

%%%%%%%%%%%%%%%%%%%%%%%%%%%%%%%%%%%%%%%%%%%%%%%%%%%%%%%%%%%%%%%%%%%%%%%
%%%%  Hypertext references for Acrobat                             %%%%
%%%%%%%%%%%%%%%%%%%%%%%%%%%%%%%%%%%%%%%%%%%%%%%%%%%%%%%%%%%%%%%%%%%%%%%
\hypersetup{
pdfauthor = {SWC},
pdftitle = {Custom Two Photon},
pdfkeywords = {optics, lenses, two photon, imaging, PMT, microscope},
pdfcreator = {LaTeX with hyperref},
pdfproducer = {dvips + ps2pdf}
           }

\begin{document}

%set the number of sectioning levels 
\setcounter{secnumdepth}{2}

\begin{center}
\textbf{\Large{Building a Custom Two Photon Microscope}}
\end{center}

\section{Introduction}
It is time to put together everything you've learned so far and build a two photon microscope. 
The microscope you will be building was designed specifically for this optics course and has the following features:

\begin{itemize}
\item A small footprint so two microscopes can be built simultaneously on a small optical table.
\item Modular design. e.g. the scanner relay optics can be assembled separately and just dropped into the microscope.
\item Light path remains low to the table for safety.
\item Low cost: almost all parts readily available from ThorLabs.
\end{itemize}

\section{IMPORTANT SAFETY INFORMATION}
Read this laser safety information before beginning. 
The following information should have been conveyed to you verbally. 
Please ask if you did not receive verbal instruction or if you have questions about laser safety. 

You will be working with a high energy pulsed laser capable of instantly blinding you should it enter your eye. 
During operation of the microscope the laser will be tuned to 920 nm which is invisible. 
Despite being invisible, the laser remains equally bright and equally dangerous.
Be very cautious around the set up:

\begin{itemize}
    \item Wear eye protection and use IR viewing cards as appropriate.
    \item Always be aware of the location of the beam and ensure everyone else in the room is also aware.
    \item Remove watches, jewelry, etc. Avoid directing the beam at shiny surfaces which could reflect it at unpredictable angles.
    \item Reduce laser power during alignment and tune the laser to visible wavelengths when possible.
    \item Shutter the beam when not using it. 
    \item Take particular care where the beam is directed upwards, such as in the periscope. 
    \item The scanners can deflect the beam by $>20$ degrees depending on the command signal. Ensure the mirrors are static and zeroed before routing the beam into the scan head for the first time. 
    \item Stand behind the scanners whilst the microscope is scanning.
    \item Use beam blocks where appropriate to keep the beam within your work area.
\end{itemize}

\clearpage

\section{General Plan}
Fig.~\ref{fig:layout} (left) shows the layout of key components on the optical table. 
The beam leaves the laser and enters a half-wave plate and polarizing beam-splitter cube that we will use to control laser power. 
The shutter is used to gate the beam for safety and not to fry the sample when you aren't scanning.
The beam proceeds to a beam expander and then on to the microscope. 
Fig.~\ref{fig:layout} (right) is a CAD model depicting the completed microscope. 
You will construct the beam expander and build the microscope. 
Since this involves a large number of parts, you will build it in stages as a series of modules then assemble those modules as a finished microscope. 
\begin{figure}[h]
\center


\caption{Left: Layout of the main lightpath. Only key components are shown. Right: CAD model of the completed microscope (minus emission detection path).}
\label{fig:layout}
\end{figure}

\clearpage

\subsubsection{Beam Expander}
First you will add the beam expander. 
The completed beam expander is shown in Fig.~\ref{fig:beamExpander}. 
Assemble the expander and place to one side: before inserting it into the light path you will need to think carefully how it will be aligned with the beam. 
The beam will need to travel down the axis of the expander and it will need to emerge collimated.
Avoid touching the lens surfaces and don't force the components together. 

You can check collimation by ensuring the beam doesn't diverge or converge at large distances from the expander. 
You can check alignment by placing two irises on the beam path downstream of where the expander will go and ensuring that the beam is undeviated when the beam expander is put into place. 
Hint: your job will be easier if the beam enters the expander parallel to the table. 

Place a temporary beam block after the telescope for safety.
What is the magnification of the expander and why might we want to expand the beam?

\begin{figure}[h]
\center



\caption{Beam expander shown assembled (top) and as components in box (bottom). Avoid touching the lens surfaces.}
\label{fig:beamExpander}
\end{figure}

\clearpage

\subsubsection{Main microscope assembly}
You can now build the skeleton of the microscope frame Fig.~\ref{fig:frame} (left) and mount it on its support pillars Fig.~\ref{fig:frame} (right).
The support pillars, coloured red, are not identical. 
The pillar for the scanner is slightly higher. 
You will find most parts in the box labeled `\textbf{2P Support Mechanics}', which also contains components for supporting the periscope.
The optional SM2 cage plate (shown in purple) is in the 21 L box and can temporarily be used to support the cage if you feel this is necessary. 

\begin{figure}[h]
\center


\caption{Microscope frame (left) alone and mounted on support pillars (right). Support pillars shown in red. Temporary and optional brace for the cage system shown in purple.}
\label{fig:frame}
\end{figure}

\subsubsection{Periscope}
The periscope brings the beam up into the scan head. 
Assemble the parts in the `\textbf{Periscope}' box such that they look as shown in Fig.~\ref{fig:periscope}. 
Depending on how the light path is arranged you might wish to alter the orientation of the upper and lower mirrors. 
There is an extra alignment iris in the periscope box, you can place this wherever you think is most helpful.
You can now attach the periscope to the microscope and support it with the components shown in red. 
You will find those in the box labeled `\textbf{2P Support Mechanics}'.
Ensure the periscope is vertical and not tilted and that the scanner enclosure is square with respect to the cage system. 
Once bolted to the table, the periscope will also stop the scanners from rotating in the SM2 cage plate to which they are screwed.
\textbf{Do not tighten the scanner hard onto the connected cage plate: it can jam. Be gentle.}

\begin{figure}[h]
\center


\caption{Periscope assembly. Support structures shown in red.}
\label{fig:periscope}
\end{figure}

\clearpage

\subsubsection{Aligning the beam with the frame}
You are now in a position to feed the the beam into the scanners. 
\textbf{Be cautious feeding the beam into the periscope: perform this step with assistance}. 
Use the provided alignment tools and your beam alignment skills to get the beam traveling straight down the middle of the microscope frame. 
\textbf{Before beginning, ensure the scanners are powered and zeroed. Always be aware of where the beam is located.}

\subsubsection{Scan Optics}
You will now assemble the scan lens and tube lens module. 
The parts you will need are in the box labeled `\textbf{2 Photon Scan Optics}' and are to be assembled as shown in Fig.~\ref{fig:scan_optics}.
Avoid touching the lens surfaces. 
Once assembled, you can drop the unit into the microscope frame. 
Ensure the beam exits the assembly collimated. 
Take care with the CDA1 drop-in hangers: tighten gently and only once they are clamped onto a rod.
What is the total expansion of the beam?

\begin{figure}[h]
\center


\caption{Scan and tube lens module.}
\label{fig:scan_optics}
\end{figure}

\clearpage

\subsubsection{Completing the excitation path}
If you had an SM2 cage plate (the one highlighted in purple) supporting the frame, you will need to remove it to add the dichroic cube (Fig.~\ref{fig:dichroic_holder}).
Think before you do this, however. 
How far should the scanner relay optics be from the scanners and how far from the tube lens should the dichroic cube be mounted?
The path of the beam through the cube is depicted in Fig.~\ref{fig:dichroic_holder} as a red line.
To help you with this step, you can move the scanners over a small scan angle whilst looking at the the beam motion. 
Use ScanImage for this, as it is has been configured to avoid large scan angles.
\textbf{Be cautious: the beam might still spill out of the scan head. Stand behind the scanners and perform this step with assistance}.
Finally, is the beam exiting the cube traveling directly downwards and so on-axis with the objective we will add?
Use two rods and the spring-loaded SM1 target to check. 

\begin{figure}[h]
\center


\caption{Dichroic cube. Image on the right shows the path of the laser beam through the component.}
\label{fig:dichroic_holder}
\end{figure}

Once you are satisfied with the alignment, you can try scanning a fluorescent plastic sample card and confirming by eye that you get fluorescence whilst the beam is moving over the sample:
\begin{itemize}
    \setlength\itemsep{0.15em}
     \item Insert the 40x objective.
     \item Add the 3-axis stage under the objective.
     \item Place a Chroma fluorescent sample card on the stage and carefully bring it up to the objective. Working distance is 2 or 3 mm. 
     \item Use water as the immersion medium.
     \item Use a low laser power and a suitable wavelength. 
     \item Start scanning and focus until you see fluorescence.
 \end{itemize}

\clearpage

\subsubsection{Adding the emission path}
You now have a functioning excitation path, but you need a detector in order to get an image. 
You will now to add a PMT with appropriate relay optics in order to capture the fluorescence on the PMT surface. 
A schematic depicting the path the emitted light will take is shown in Fig.~\ref{fig:dichroic_holder_paths}.
Think carefully what lens or lenses you need to add before the PMT. 
Hint: what should be conjugate with the PMT?
What other optical element do you need to add before the PMT?

The PMT is \textbf{delicate}. 
Do not expose it to even room light when powered on, as this will damage the photocathode. 
Get assistance to power the PMT and hook up the amplifier. 
\begin{figure}[h]
\center

\caption{Path of the emitted light through the dichroic cube. The cube's side-plate is removed to show the dichroic mirror itself. The illustration also shows the objective (transparent) and PMT holder (to the far right).}
\label{fig:dichroic_holder_paths}
\end{figure}

\subsubsection{Obtaining an image}
Time to obtain some images!
\begin{itemize}
\item Image the fluorescent sample card. 
\textbf{Use low laser power as this sample is very bright}. 
Use 1x zoom. 
This sample provides information on how uniform the illumination is.

\item Image the $25~\mu m$ pitch copper EM grid at 1x, 2x, and 3x zoom. 
How many microns per pixel do you get?
Use any wavelength at low power. 

\item Image some pollen grains. 
Try focusing up and down through them to get a feeling for the optical sectioning ability of your microscope. 
The micrometer advances the sample $500~\mu m$ per revolution. 

\item Image a zebrafish larva!

\end{itemize}

\end{document}

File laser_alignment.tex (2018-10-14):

%%%%%%%%%%%%%%%%%%%%%%%%%%%%%%%%%%%%%%%%%%%%%%%%%%%%%%%%%%%%%%%%%%%%%%%
%%%%  Load the document class and packages                         %%%%
%%%%%%%%%%%%%%%%%%%%%%%%%%%%%%%%%%%%%%%%%%%%%%%%%%%%%%%%%%%%%%%%%%%%%%%
\documentclass[a4paper]{report}
\usepackage{epsfig}            % to insert PostScript figures
\graphicspath{ 
  {figures/} 
}

%Change figure names
\renewcommand{\figurename}{Fig}

\usepackage[bf,footnotesize]{caption} % make captions small and label bold

\addtocounter{chapter}{1} %Because starting at zero is silly
\makeatletter
\renewcommand{\thesection}{\@arabic\c@section}
\renewcommand{\thefigure}{\@arabic\c@figure}
\makeatother

\usepackage[a4paper,margin=2.7cm,tmargin=2.5cm,bmargin=2.5cm]{geometry} 
\usepackage{textcomp}          % To make nice degree symbols and others\usepackage[bf,footnotesize]{caption} % make captions small and label bold
\usepackage{wrapfig}
%to produce the clickable references along the left in Acroread. This
%package must be included last. 
\usepackage[ps2pdf,bookmarks=TRUE]{hyperref} 

%%%%%%%%%%%%%%%%%%%%%%%%%%%%%%%%%%%%%%%%%%%%%%%%%%%%%%%%%%%%%%%%%%%%%%%
%%%%  Hypertext references for Acrobat                             %%%%
%%%%%%%%%%%%%%%%%%%%%%%%%%%%%%%%%%%%%%%%%%%%%%%%%%%%%%%%%%%%%%%%%%%%%%%
\hypersetup{
pdfauthor = {TENSS},
pdftitle = {Laser Alignment},
pdfkeywords = {lasers,optics,alignment,reflection,microscopy},
pdfcreator = {LaTeX with hyperref},
pdfproducer = {dvips + ps2pdf}
           }

\begin{document}

%set the number of sectioning levels 
\setcounter{secnumdepth}{2}

\begin{center}
\textbf{\Large{Laser Routing and Alignment}}
\end{center}

A thorough understanding of beam alignment is critical for building a scanning microscope. 
`Beam alignment' refers to the process of routing a laser beam precisely along a defined path. 
Optical elements such as lenses are generally inserted into the path defined by the beam. 
In most situations the laser is in a fixed position and is directed using flat \textit{first surface} mirrors.
The aim of this exercise is to redirect a laser beam through a specific line at a specific height above the table using two mirrors.
Do not touch the reflective mirror surfaces!

\section{Aligning the beam through a path defined by two points}
Your goal is to set up a laser pointer, two mirrors, and two irises in order to achieve the state shown in Fig.~\ref{fig:ex1}. 
The beam should pass straight through the irises, the exact locations of the other components is not important. 
The mirror holder mounted on the rail ($mirror_2$) should be a KM100CP/M. 
Separate the irises by as much space as possible and keep $mirror_2$ fairly close to $iris_1$.
Once this is established, add $mirror_1$ such that it is square with $mirror_2$ and at least about $10~cm$ away from it. 
Finally, set up the laser pointer such that the beam hits $mirror_1$.
Now the fun starts\ldots

\begin{figure}[h]
\center


\caption{Your goal is to send the beam through the two irises by altering the tilt of the two mirrors.}
\label{fig:ex1}
\end{figure}

The goal is to have the beam pass through the two iris centres without moving the laser pointer. 
In most cases it will be possible to complete the exercise simply by altering the tilt of the mirrors and rotating the mirror posts in their holders. 
If the mirrors are initially very mis-positioned you might also need to translate them across the table. 
To complete the exercise you will need to understand the following keys points:

\begin{enumerate}
\setlength\itemsep{0.1em}
\item Adjusting $mirror_1$ \textit{translates} the beam across the surface of $mirror_2$.
\item Adjusting $mirror_2$ alters \textit{the angle} with which the beam goes through the irises. 
\item As a consequence of (1), you adjust $mirror_1$ to pass the beam through $iris_1$.
\item As a consequence of (2), you adjust $mirror_2$ to pass the beam through $iris_2$.
\item Iteratively adjusting the two mirrors will always allow the beam to pass through both irises, assuming that there exists a region of $mirror_2$ that falls along the axis defined by the two irises. 
\end{enumerate}

Here is how you will implement the above:

\begin{enumerate}
\item Close $iris_1$ and adjust $mirror_1$ to position the beam at the centre of $iris_1$. \textit{Use the adjustment screws for fine positioning only. For coarse postioning, rotate the post.}
\item Open $iris_1$ and rotate $mirror_2$ to position beam at centre of closed $iris_2$. 
The process of doing this will move the beam away from the centre of $iris_1$. 
The degree to which this happens depends on the distance between $mirror_2$ and $iris_1$.
\item Close $iris_1$ and assess the beam position. If not aligned, repeat steps 1 \& 2. 
If aligned, stop. 
\end{enumerate}

\subsubsection{Tips}
\begin{itemize}
\item If after repeated attempts at alignment you keep failing, this indicates that a mirror (probably mirror 2) is mis-positioned. 
\item Only use right angles. 
Whilst it is possible to use very acute angles and still solve the alignment task, you will have a larger mirror area to play with if you reflect the beam at 90 degree angles.
\item Manage your real-estate: You will notice that sometimes, the beam will fall off $mirror_2$. This problem can be solved by using a larger mirror, or by translating $mirror_2$ in the direction where the beam fell off its edge.
\end{itemize}

\section{Getting the beam parallel with the table}
Your 2-photon laser has arrived and it's time to begin building your microscope's light path. 
To make your life easier, you decide to use two mirrors to ensure that the beam emerging from the laser comes out parallel with the optical table and at a height suitable for your lenses and other optical elements. 

Set up your laser pointer and two mirrors as shown in Fig.~\ref{fig:ex2}. 
The mirrors can be as close to the laser as you like. 
Place an iris on a post holder and use a post base to improve stability. 
Do not bolt the iris to the table.
This single iris defines the height at which you want the beam to be at all locations on the optical table. 
Based on what you learned in Exercise~1, use the iris and the two mirrors to ensure the beam is parallel with the table at the height defined by your iris. 
Hint: all you're allowed to do is change the tilt of the two mirrors and translate the iris across the table.

\begin{figure}[h]
\center

\caption{Using two mirrors to ensure the beam is parallel with the table. }
\label{fig:ex2}
\end{figure}

\end{document}

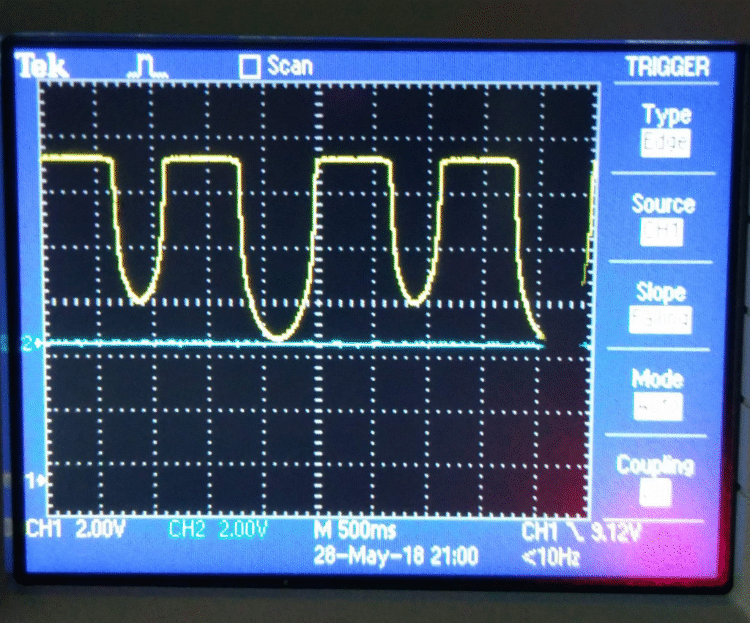
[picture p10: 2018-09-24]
scanningFigs/trace_photodiode.png

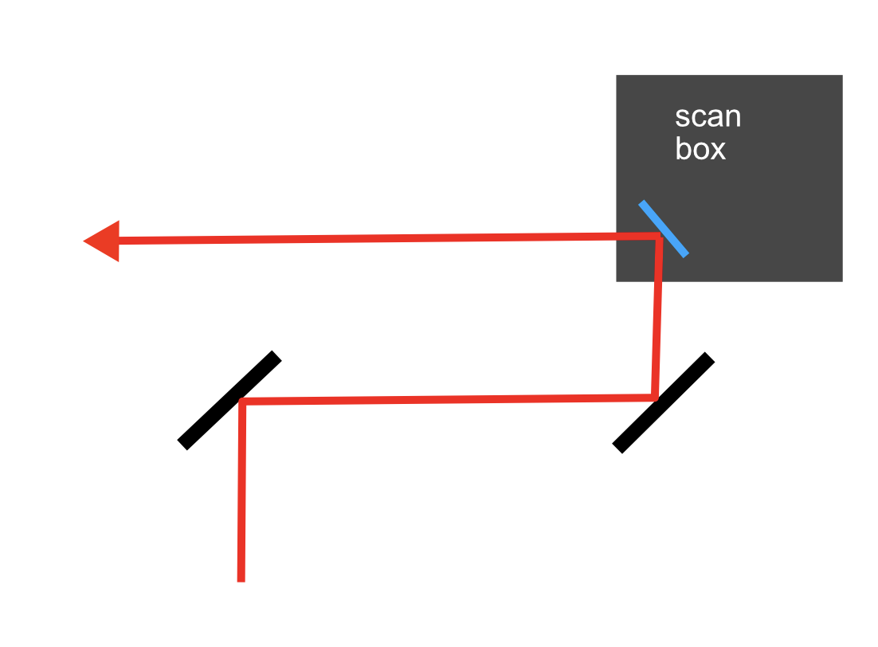
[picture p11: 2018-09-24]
scanningFigs/beamintoscanner.png

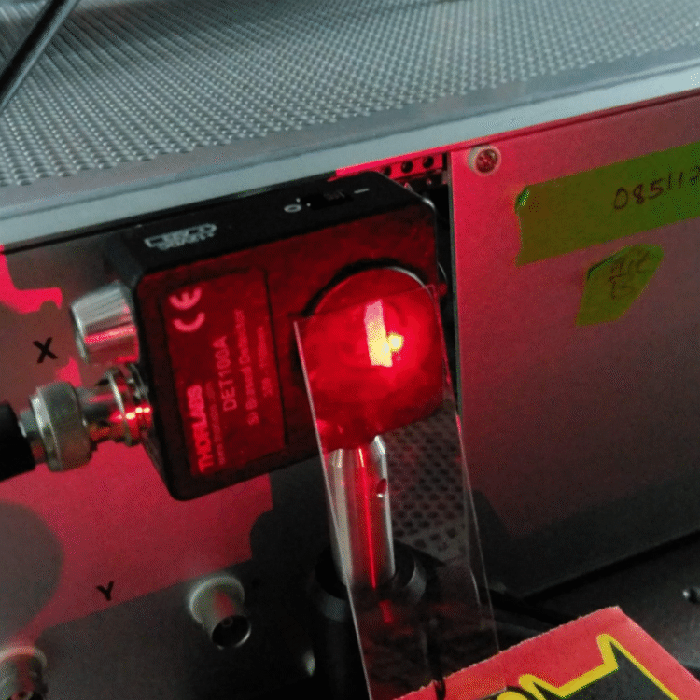
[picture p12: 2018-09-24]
scanningFigs/PhotoDiode_with_tape.png

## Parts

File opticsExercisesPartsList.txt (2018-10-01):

Bench optics parts list

The following is the parts list used at the Sainsbury Wellcome Centre (UCL) to complete 
the bench optics exercises. Some of the more expensive parts are optional but nice to 
have. The parts list includes more parts than are needed in order to provide students 
with multiple ways of solving the same problem. Some parts listed below are re-used in
other exercises. 

Parts are from ThorLabs unless otherwise specified. Imperial part numbers are listed. 

* General optomechanics
The following are used to mount optical 

1x XT66DP-1000 optical rail 
1x 500 mm rail
4x CL5 clamps
1x XE25CL2 clamp
10x XT66C4 clamping platforms
2x packs of 5 post holders PH50-P5 (10 in total)
2x PH40 post holders
1x PH30 post holder
3x TR75 75 mm posts
7x TR50 50 mm posts
4x TR40 40 mm posts
4x TR30 30 mm posts
4x LMR2 2" lens holders (post mountable)
2x CP02 30 mm cage plate for 1" optics
2x CP02T thick 30 mm cage plate for 1" optics
1x SM1L10 1" SM1 lens tube
1x SM1L05 0.5" SM1 lens tube
1x SM1L03 0.3" SM1 lens tube
1x LCP08 60 mm Cage Plate, SM2 Threads, Enhanced Clamping, 0.5" Thick (optional)
1x LCP02 30 mm to 60 mm Cage Plate Adapter (optional)
1x SM1T2 to couple camera to cageplate
1x SM1A9 to couple camera to an SM1 tube

* Sample holders
1x DH1 filter holder
1x EDU-VS1 Post-Mountable White Polystyrene Viewing Screen (optional)
1x XYFM1 Translatable slide holder (optional)
1x SMIZ Linear translation stage for objective (optional but recommended)

* Optics
More than enough lenses are included to allow for experimentation. 
These are cheaper lenses and are to be used for the bench optics. 
In some cases either plano-convex or bi-convex are listed. Either will work.
1x LB1761 1" f=25 mm
1x LB1811 1" f=35 mm
2x LA1401 or LB1723 2" f=60 mm 
1x LA1050 or LB1630 2" f=100 mm
1x LA1979 or LB1199 2" f=200 mm
1x LA1256 or LB1917 2" f=300 mm
1x LC1715 1" f=-50 mm
1x f=300 mm SM1 for fluorescence (tube lens)

1x Olympus 4X objective (WD RMS4X) and RMS to SM1 coupler (SM1A3).

* Misc.
1x RA180
1x RA90 post clamps
2x post-mounted iris diaphragms (ID25)
2x R2 post collars (optional)
Each kit will need about 15 cap screws in each of a range of lengths from about 10 mm to 20 mm. 
Screws should be M6 or 1/4"-20 depending on your equipment.

* Cage system parts (optional)
These parts are used to make cage systems, which are mainly important for 
fluoresence imaging and building alignment jigs. For the bench optics 
exercises alone you need purchase only the ER2 rods
2x ER1.5 rods
1x ER2-P4
1x ER3-P4
1x ER4-P4
1x ER6-P4

Light sources -- TODO
LEDs (ADD THIS) 

Coverslips and a marker pen.

Slides to image. 

Electron microscopy grids of known pitch might be useful but aren't explicitly used in these exercises.
A 1 to 2 m tape measure. 

A laser pointer that fits into an RA180 post clamp that attaches to one end of a post.

* Tools
1x Lens wrench for SM1 SPW606
1x Lens wrench for SM2: SPW604
1x Hex keys such as CCHK or TC2 (TC3 for metric). 
1x BD-050 0.050" Balldriver for 4-40 Setscrews (used for cage system set screws)
1x LMR2AP alignment target (optional)
1x MFT1 1m measuring tape or a longer one (up to about 2 m) from a different supplier
1x Wera hex key set (not from Thor - optional)

* For laser alignment (beam walking) exercise
1x KM100CP Post-Centered mirror mount
2x KM100 regular mirror mounts

* General parts for 2p
2x SM1EC2B Snap-On Plastic Dust Cap for SM1 Lens Tubes, 5 Pack

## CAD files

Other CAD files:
CAD_files/BA1_M-Solidworks.ipt
CAD_files/CP02_M-Solidworks.ipt
CAD_files/ER4-Solidworks.ipt
CAD_files/GCM102_M-Solidworks.ipt
CAD_files/ID25_M-Solidworks.ipt
CAD_files/Iris_On_Carriage.iam
CAD_files/KM100-Solidworks.ipt
CAD_files/KM100CP_M-Solidworks.ipt
CAD_files/LCP02_M-Solidworks.ipt
CAD_files/LCP08_M-Solidworks.ipt
CAD_files/LCP11_M-Solidworks.ipt
CAD_files/LM2_lensholder_on_mount.iam
CAD_files/LMR2_M-Solidworks.ipt
CAD_files/Laser_alignment.iam
CAD_files/MB60120_M-Solidworks.ipt
CAD_files/Mirror_on_carriage.iam
CAD_files/MountedScanners.iam
CAD_files/OldVersions/LM2_lensholder_on_mount.0002.iam
CAD_files/OldVersions/RailAndMirror.0001.iam
CAD_files/OldVersions/SM1_scanlensholder_on_mount.0002.iam
CAD_files/OldVersions/ScannerMountingOption1.0001.iam
CAD_files/OldVersions/ScannerSetUp.0001.iam
CAD_files/PF1011-F01-Solidworks.ipt
CAD_files/PH50_M-Solidworks.ipt
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

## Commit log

2018-09-24 Add CAD drawing to laser alignment handout.
    [BA1_M-Solidworks.ipt, ID25_M-Solidworks.ipt, Iris_On_Carriage.iam, KM100-Solidworks.ipt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]
2018-09-24 Update to new benchtop scanning exercises and add CAD drawings.
    [CP02_M-Solidworks.ipt, ER4-Solidworks.ipt, GCM102_M-Solidworks.ipt, LCP02_M-Solidworks.ipt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]
2018-10-05 Split illumination of the sample into a separate file.
2018-10-13 Change simple lens image to one with an idealised thin lens
2019-10-15 changed major things: made flow more 'uniform', from setting up illumination all the way to koehler without unbuilding and rebuilding as suggested in previous version. added more questions and points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
